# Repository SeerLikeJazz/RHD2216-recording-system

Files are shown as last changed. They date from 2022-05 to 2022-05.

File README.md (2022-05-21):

> 2022.05.21，上海，疫情在家，整理一下研究生期间的部分工作……

*Project was part of my work while at:*
* [EE-MEMS LAB](https://mems.sjtu.edu.cn/)
* Department of Micro/Nano Electronics
* Shanghai Jiao Tong University
* 2016.09-2019.03
### 探针型柔性MEMS脑机接口器件及采集电路研究
#### 系统介绍
* 研制了一种超薄的柔性探针型神经信号采集电极。
* 搭建了植入式神经信号采集电路的系统平台。
* 利用研制的柔性探针型神经信号采集电极和神经信号采集电路的系统平台做了体外测试验证实验。
#### 采集电路
电路主要包括Intan Technologies公司的16通道前端微弱生理信号采集芯片RHD2116，核心控制单元采用ST公司主频168M的STM32F407微控制器，数据传输采用内部集成全硬件TCP/IP协议栈+MAC+PHY以太网接口芯片W5500，通过UDP协议的方式实现硬件系统与上位机通信。

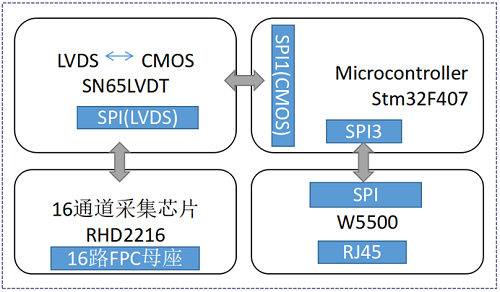
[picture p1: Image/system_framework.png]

> 系统框图

电路尺寸4.2cm x 4.2cm，重量22g（包含电池），可以非常轻便地用于脑机接口应用和生物学实验。实验表明，16通道的采集系统输入噪声低至7 μV，每通道采样频率高达20 kHz，采样分辨率16位，满足植入式神经信号采集的要求。

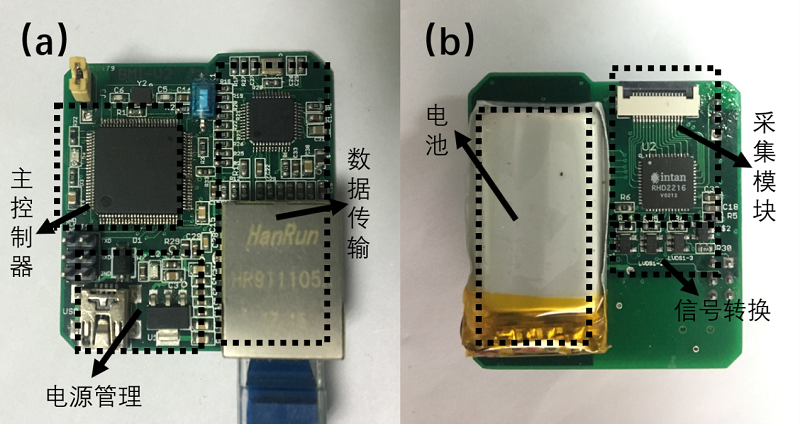
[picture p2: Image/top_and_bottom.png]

> 硬件顶、底视图

#### 柔性电极
器件整体全部采用生物相容性材料，Au（厚度300nm）作为引线、电极点和焊盘，Parylene（厚度4μm）作为基底和绝缘层，PEG作为粘结材料贴附电极于PI管上，PI管（外径330μm）用作辅助植入的支撑材料。

通过电化学沉积导电聚合物PEDOT:PSS来提高了电极的电化学性能，并通过500次的循环伏安测试和10分钟的超声处理，验证了修饰后的电极的电化学稳定和聚合物结合力稳定性，测试并分析了电极的伏安特性和电化学阻抗谱。

研究了通过生物相容性的材料和PI管的组合，改进了柔性电极的准确植入位置的方法。

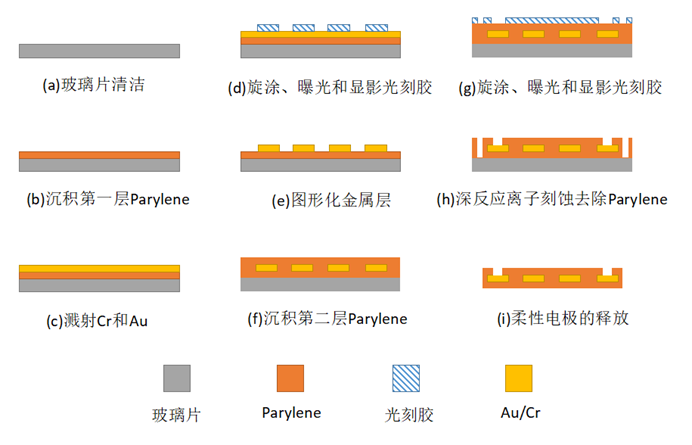
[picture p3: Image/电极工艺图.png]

> 电极工艺图

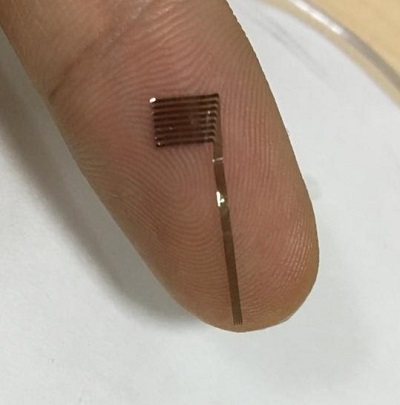
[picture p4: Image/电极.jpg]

> 电极实物图

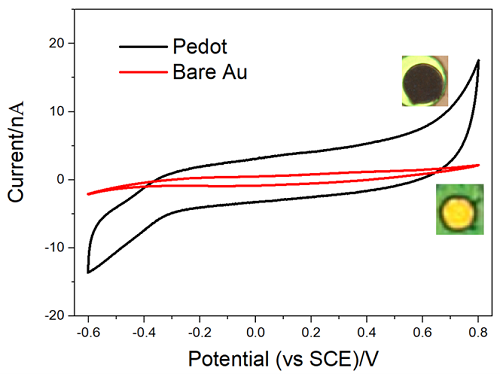
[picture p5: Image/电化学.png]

> 电化学测试

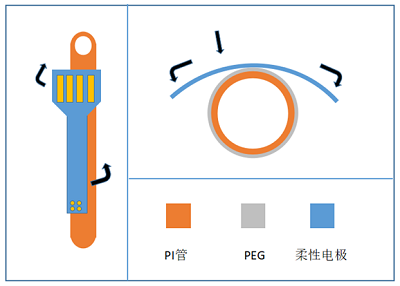
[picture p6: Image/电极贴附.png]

> 电极贴附示意图

#### 实验测试
为了验证从电极前端到采集电路后端整个系统的准确性和功能稳定性，使用琼脂和PBS溶液模拟脑组织的环境，验证柔性微电极的准确植入性，辅助使用PI管和柔性电极在环境中的分离状况；使用微小信号发生器模拟了神经信号的幅值和频率，在体外模拟的脑组织环境中测试了信号采集、数据预处理、数据传输到上位机和上位机实时波形显示的在线实验。

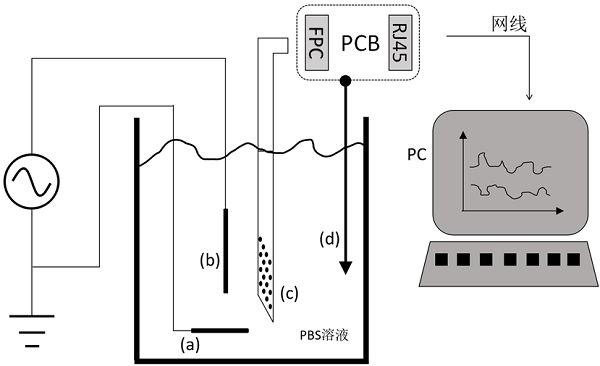
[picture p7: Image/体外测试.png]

> 测试实验示意图

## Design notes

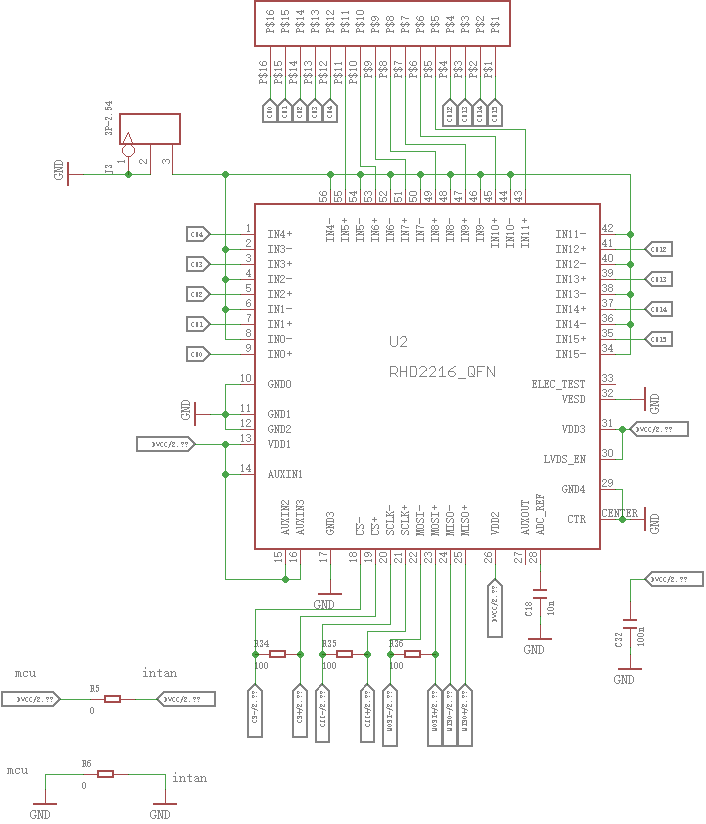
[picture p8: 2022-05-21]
Hardware/sheet 4-RHD2216.png

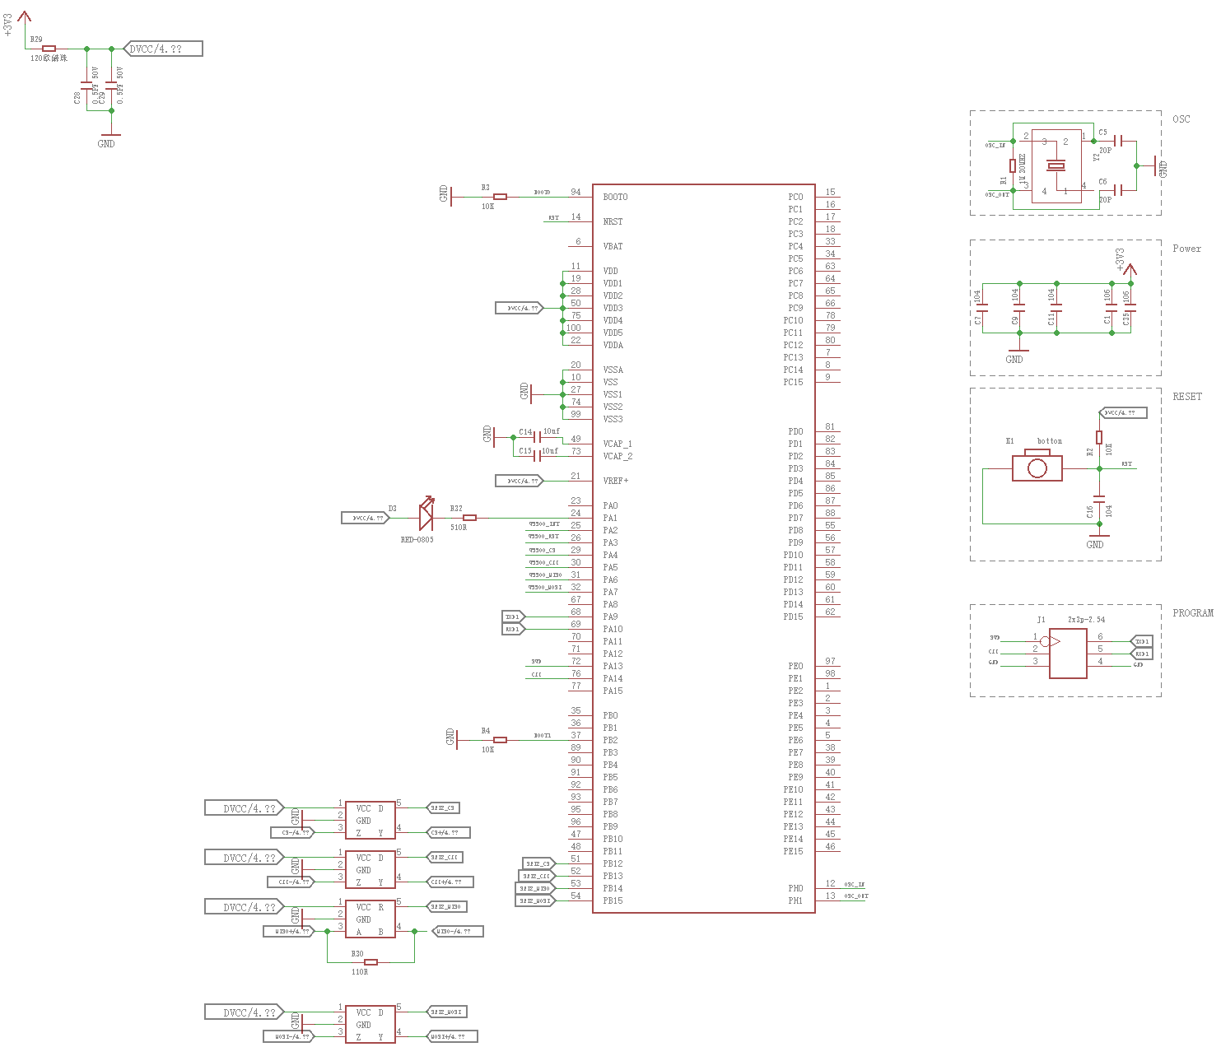
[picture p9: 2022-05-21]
Hardware/sheet 2-Mcu.png

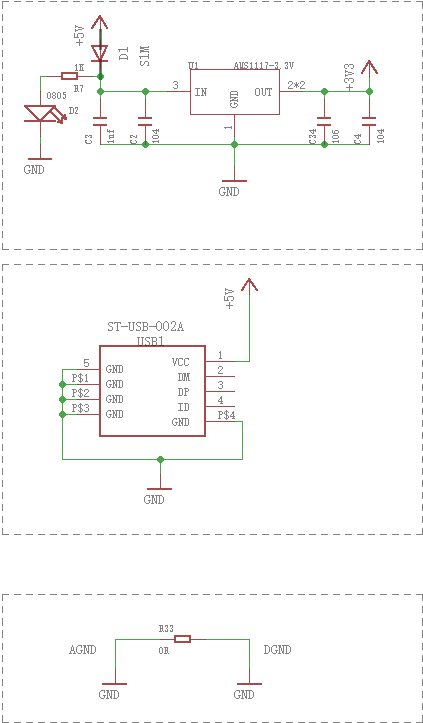
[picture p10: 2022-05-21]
Hardware/sheet 1-Power.png

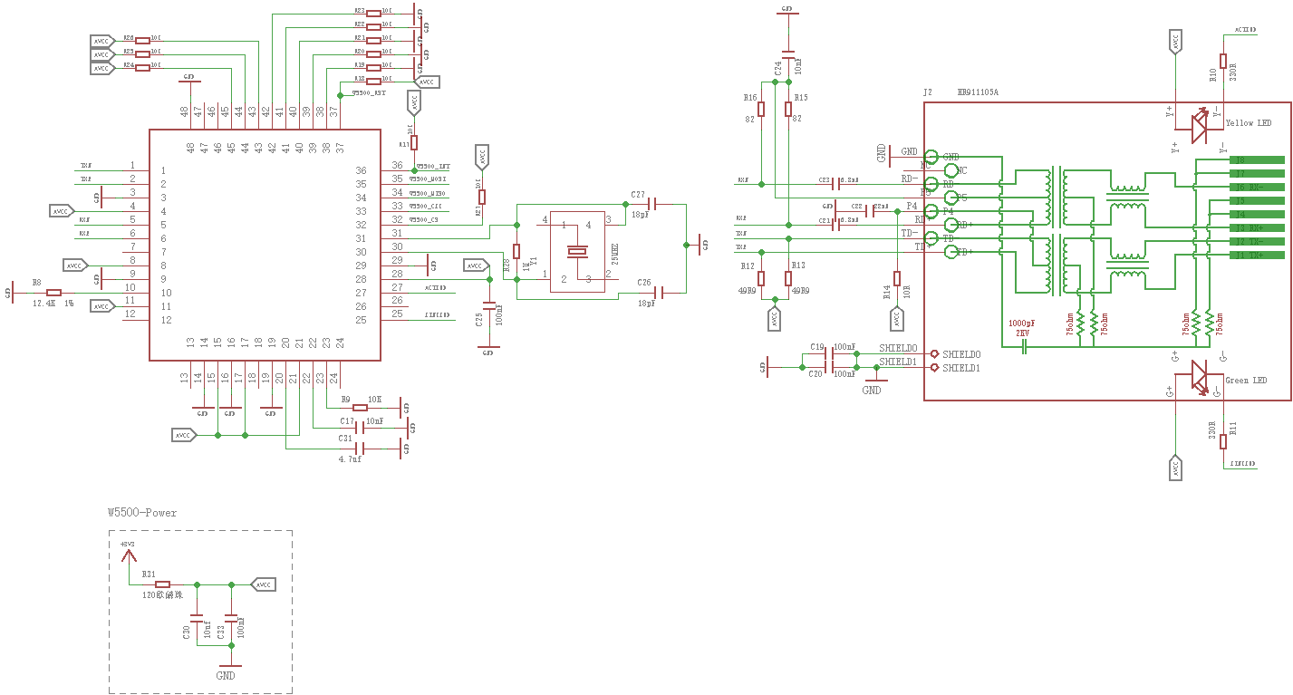
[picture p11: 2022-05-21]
Hardware/sheet 3-W5500.png

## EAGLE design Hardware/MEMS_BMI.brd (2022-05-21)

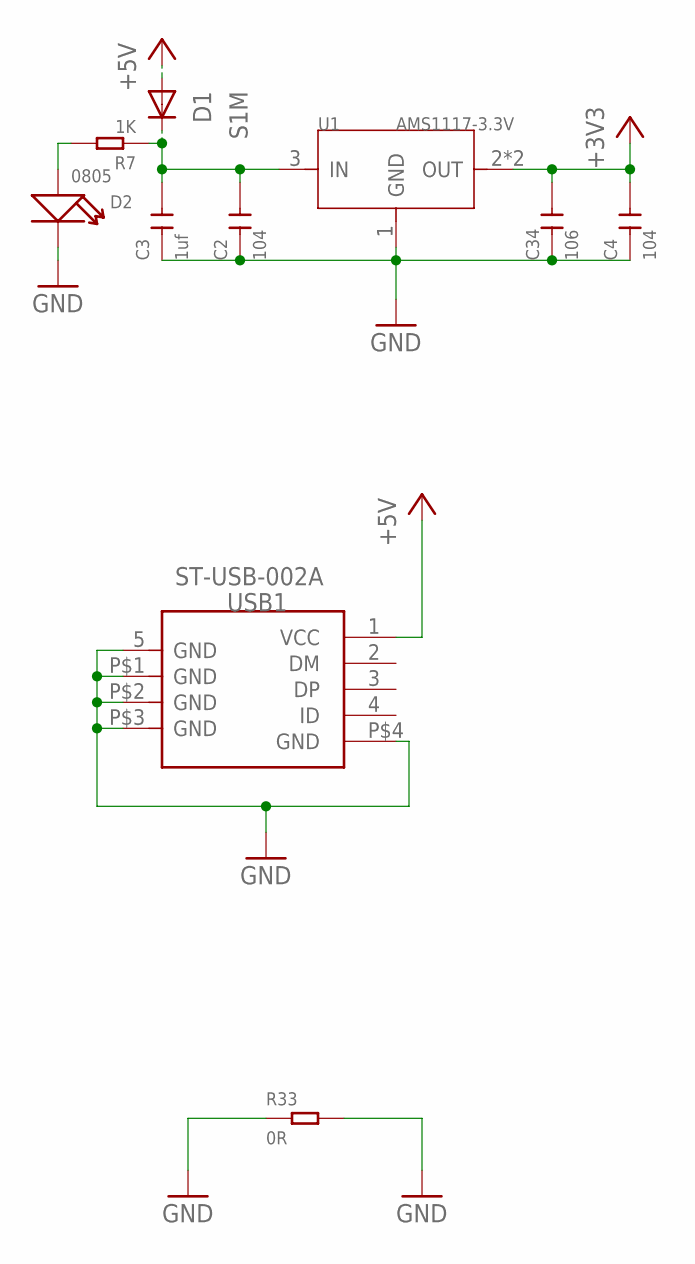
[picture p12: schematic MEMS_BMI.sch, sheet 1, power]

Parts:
C2, C4: 104; C0603
C3: 1uf; C0805
C34: 106; C0805
D1: S1M; SMA
D2: 0805; LED-0805
R7: 1K; R0603
R33: 0R; R0603
U1: AMS1117-3.3V; SOT-223
USB1: ST-USB-002A; MINIUSB5+4P-SMD-0.8-90D

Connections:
+3V3: C4.2, C34.2, U1.2 (OUT), U1.TER (OUT); also elsewhere on the board
+5V: D1.A, USB1.1 (VCC)
GND: C2.1, C3.1, C4.1, C34.1, D2.-, R33.1, R33.2, U1.1 (GND), USB1.5 (GND), USB1.P$1 (GND), USB1.P$2 (GND), USB1.P$3 (GND), USB1.P$4 (GND); also elsewhere on the board
unnamed: C2.2, C3.2, D1.C, R7.1, U1.3 (IN)
unnamed: D2.+, R7.2

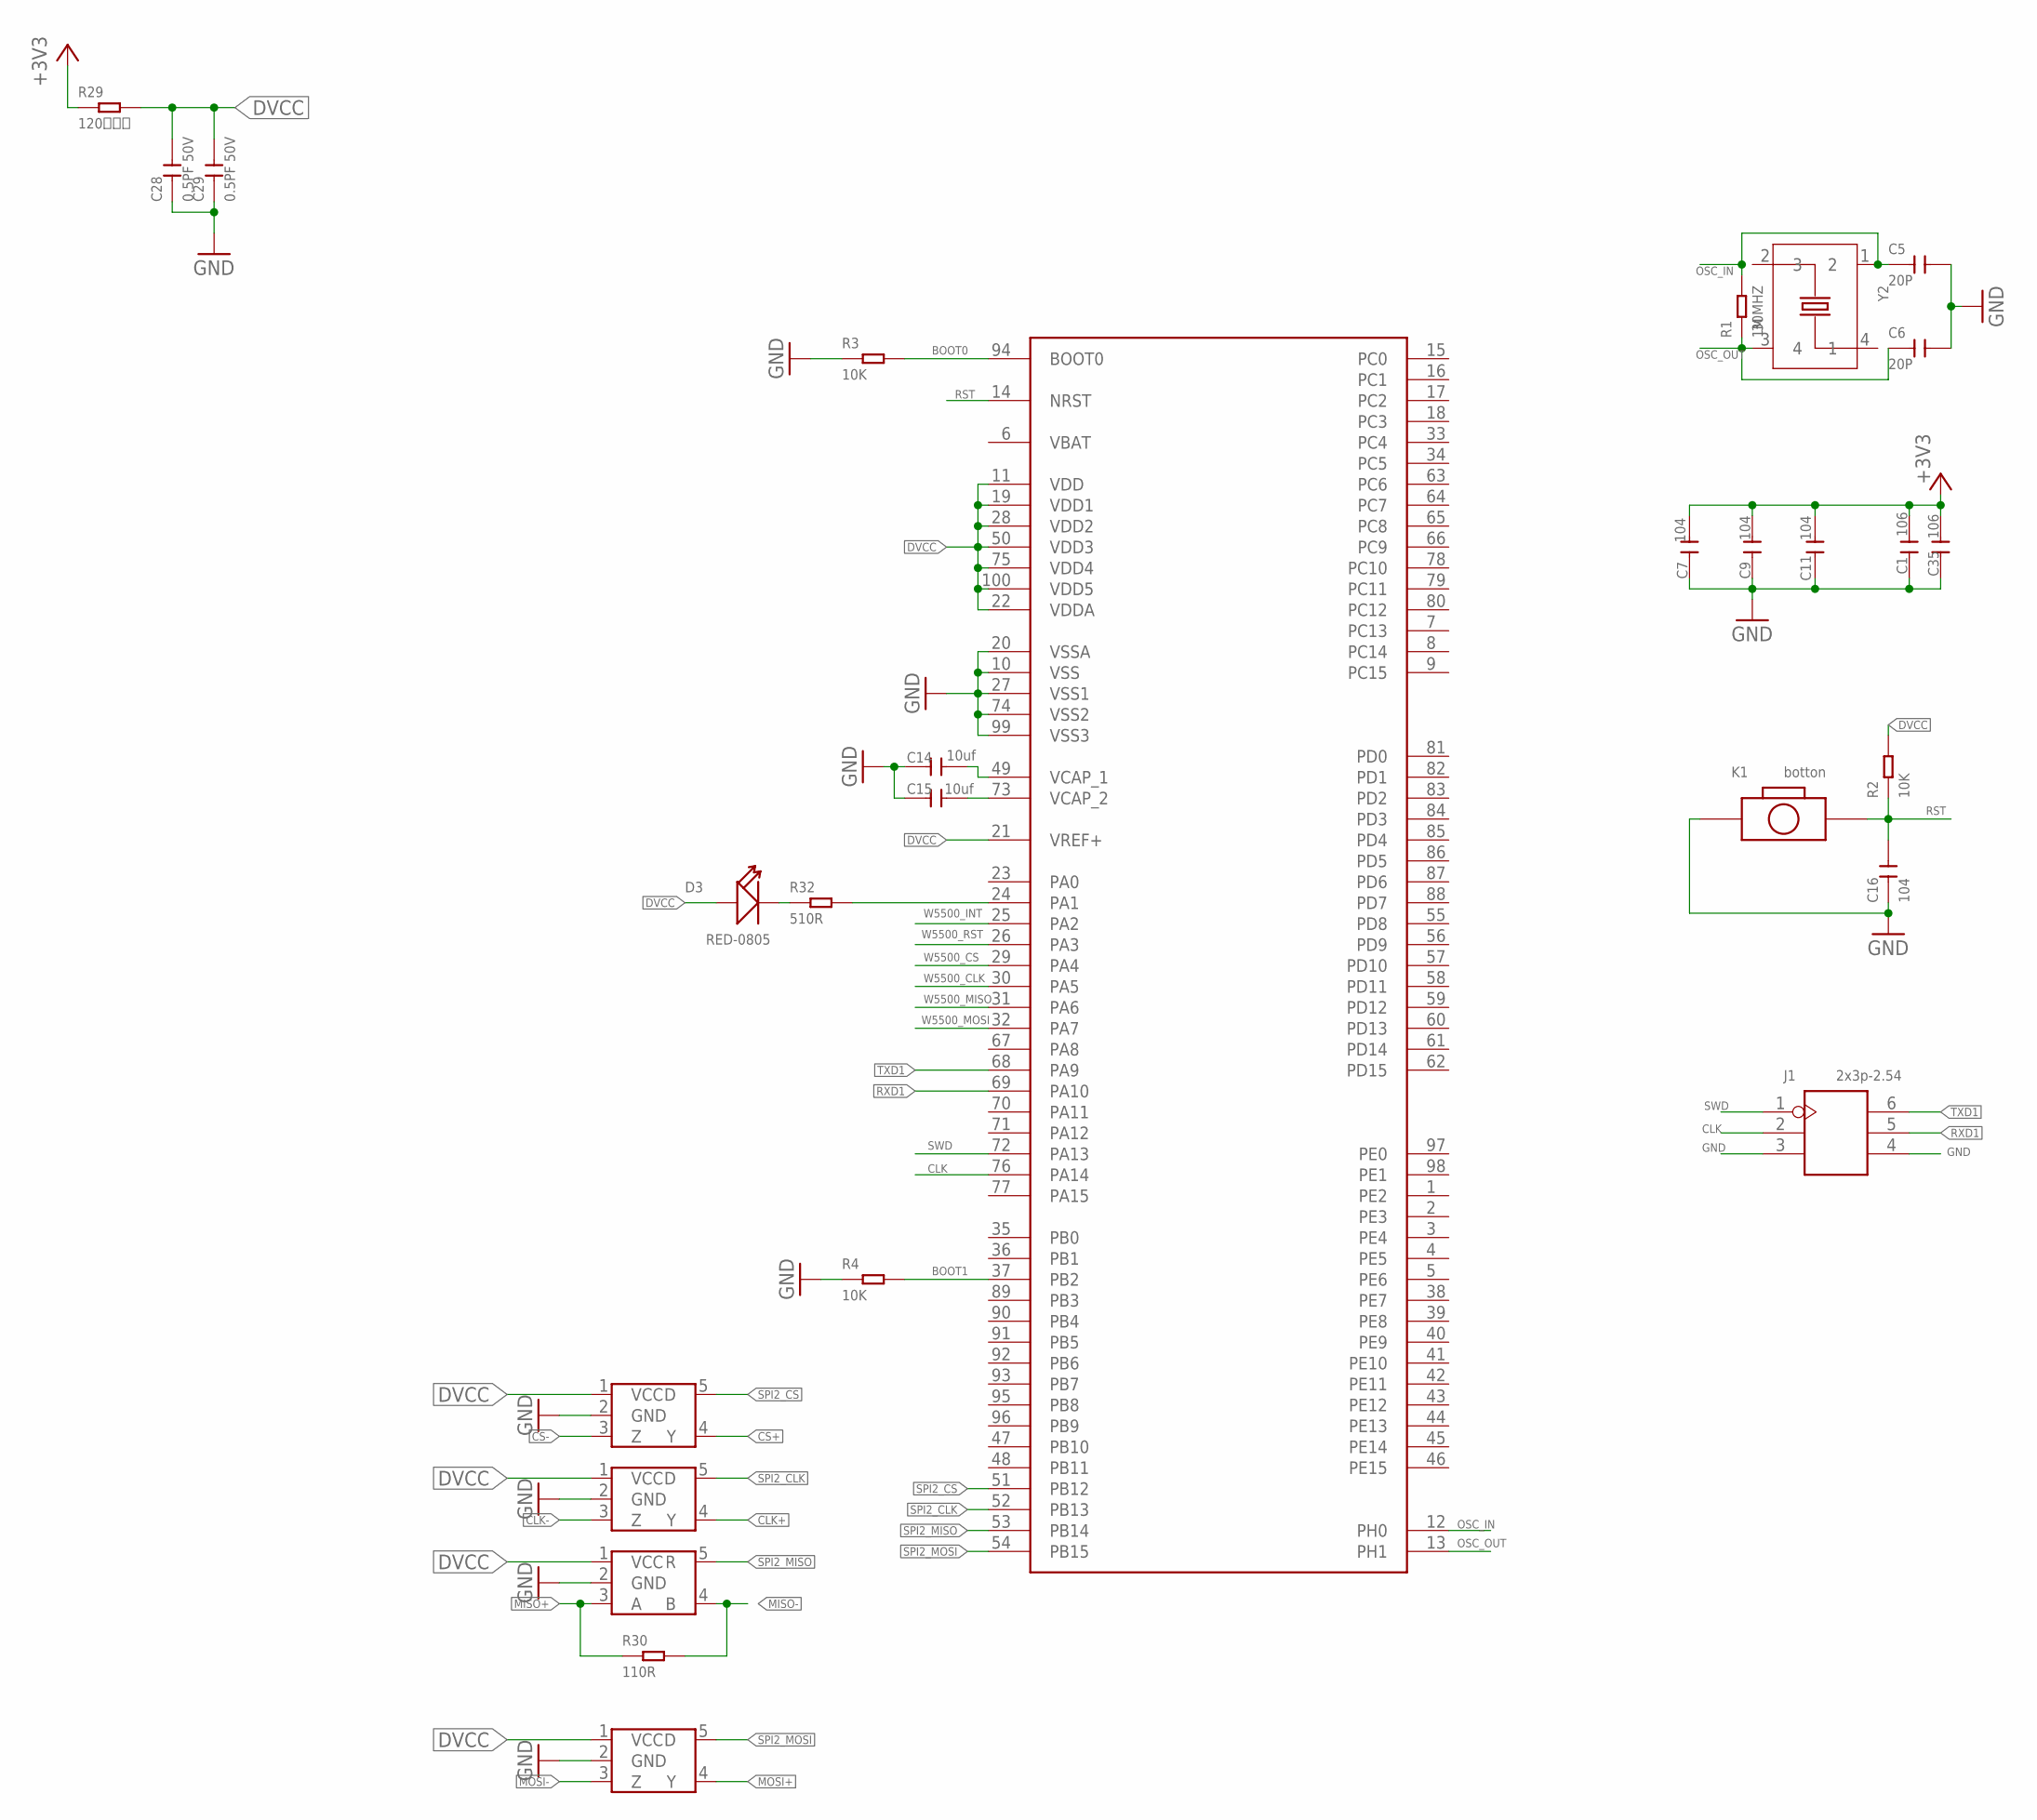
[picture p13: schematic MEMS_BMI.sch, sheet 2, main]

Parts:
C1, C35: 106; C0805
C5, C6: 20P; C0603
C7, C9, C11, C16: 104; C0603
C14, C15: 10uf; C0805
C28, C29: 0.5PF 50V; C0603
D3: RED-0805; LED-0805
J1: 2x3p-2.54; H2X3-2.54
K1: botton; SW2-SMD-3.0X6.0*2.5
LVDS1-1, LVDS1-2, LVDS1-3: SN65LVDS1; DBV_R-PDSO-G5
R1: 1M; R0603
R2, R3, R4: 10K; R0603
R29: 120欧磁珠; R0603
R30: 110R; R0603
R32: 510R; R0603
U$1: STM32F40XSTM32D40X; LQFP100
U$2: SN65LVDS2; DBV_R-PDSO-G5
Y2: 30MHZ; X4-SMD-3.2X2.5X0.7MM

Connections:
+3V3: C1.2, C7.1, C9.1, C11.1, C35.2, R29.1; also elsewhere on the board
BOOT0: R3.2, U$1.94 (BOOT0)
BOOT1: R4.2, U$1.37 (PB2)
CLK: J1.2, U$1.76 (PA14)
CLK+: LVDS1-2.4 (Y); also elsewhere on the board
CLK-: LVDS1-2.3 (Z); also elsewhere on the board
CS+: LVDS1-1.4 (Y); also elsewhere on the board
CS-: LVDS1-1.3 (Z); also elsewhere on the board
DVCC: C28.2, C29.2, D3.+, LVDS1-1.1 (VCC), LVDS1-2.1 (VCC), LVDS1-3.1 (VCC), R2.2, R29.2, U$1.11 (VDD), U$1.19 (VDD1), U$1.21 (VREF+), U$1.22 (VDDA), U$1.28 (VDD2), U$1.50 (VDD3), U$1.75 (VDD4), U$1.100 (VDD5), U$2.1 (VCC); also elsewhere on the board
GND: C1.1, C5.2, C6.2, C7.2, C9.2, C11.2, C14.1, C15.1, C16.1, C28.1, C29.1, C35.1, J1.3, J1.4, K1.1, LVDS1-1.2 (GND), LVDS1-2.2 (GND), LVDS1-3.2 (GND), R3.1, R4.1, U$1.10 (VSS), U$1.20 (VSSA), U$1.27 (VSS1), U$1.74 (VSS2), U$1.99 (VSS3), U$2.2 (GND); also elsewhere on the board
MISO+: R30.1, U$2.3 (A); also elsewhere on the board
MISO-: R30.2, U$2.4 (B); also elsewhere on the board
MOSI+: LVDS1-3.4 (Y); also elsewhere on the board
MOSI-: LVDS1-3.3 (Z); also elsewhere on the board
unnamed: C15.2, U$1.73 (VCAP_2)
unnamed: C14.2, U$1.49 (VCAP_1)
unnamed: D3.-, R32.1
unnamed: R32.2, U$1.24 (PA1)
OSC_IN: C5.1, R1.2, U$1.12 (PH0), Y2.1 (2)
OSC_OUT: C6.1, R1.1, U$1.13 (PH1), Y2.3 (4)
RST: C16.2, K1.2, R2.1, U$1.14 (NRST)
RXD1: J1.5, U$1.69 (PA10)
SPI2_CLK: LVDS1-2.5 (D), U$1.52 (PB13)
SPI2_CS: LVDS1-1.5 (D), U$1.51 (PB12)
SPI2_MISO: U$1.53 (PB14), U$2.5 (R)
SPI2_MOSI: LVDS1-3.5 (D), U$1.54 (PB15)
SWD: J1.1, U$1.72 (PA13)
TXD1: J1.6, U$1.68 (PA9)
W5500_CLK: U$1.30 (PA5); also elsewhere on the board
W5500_CS: U$1.29 (PA4); also elsewhere on the board
W5500_INT: U$1.25 (PA2); also elsewhere on the board
W5500_MISO: U$1.31 (PA6); also elsewhere on the board
W5500_MOSI: U$1.32 (PA7); also elsewhere on the board
W5500_RST: U$1.26 (PA3); also elsewhere on the board

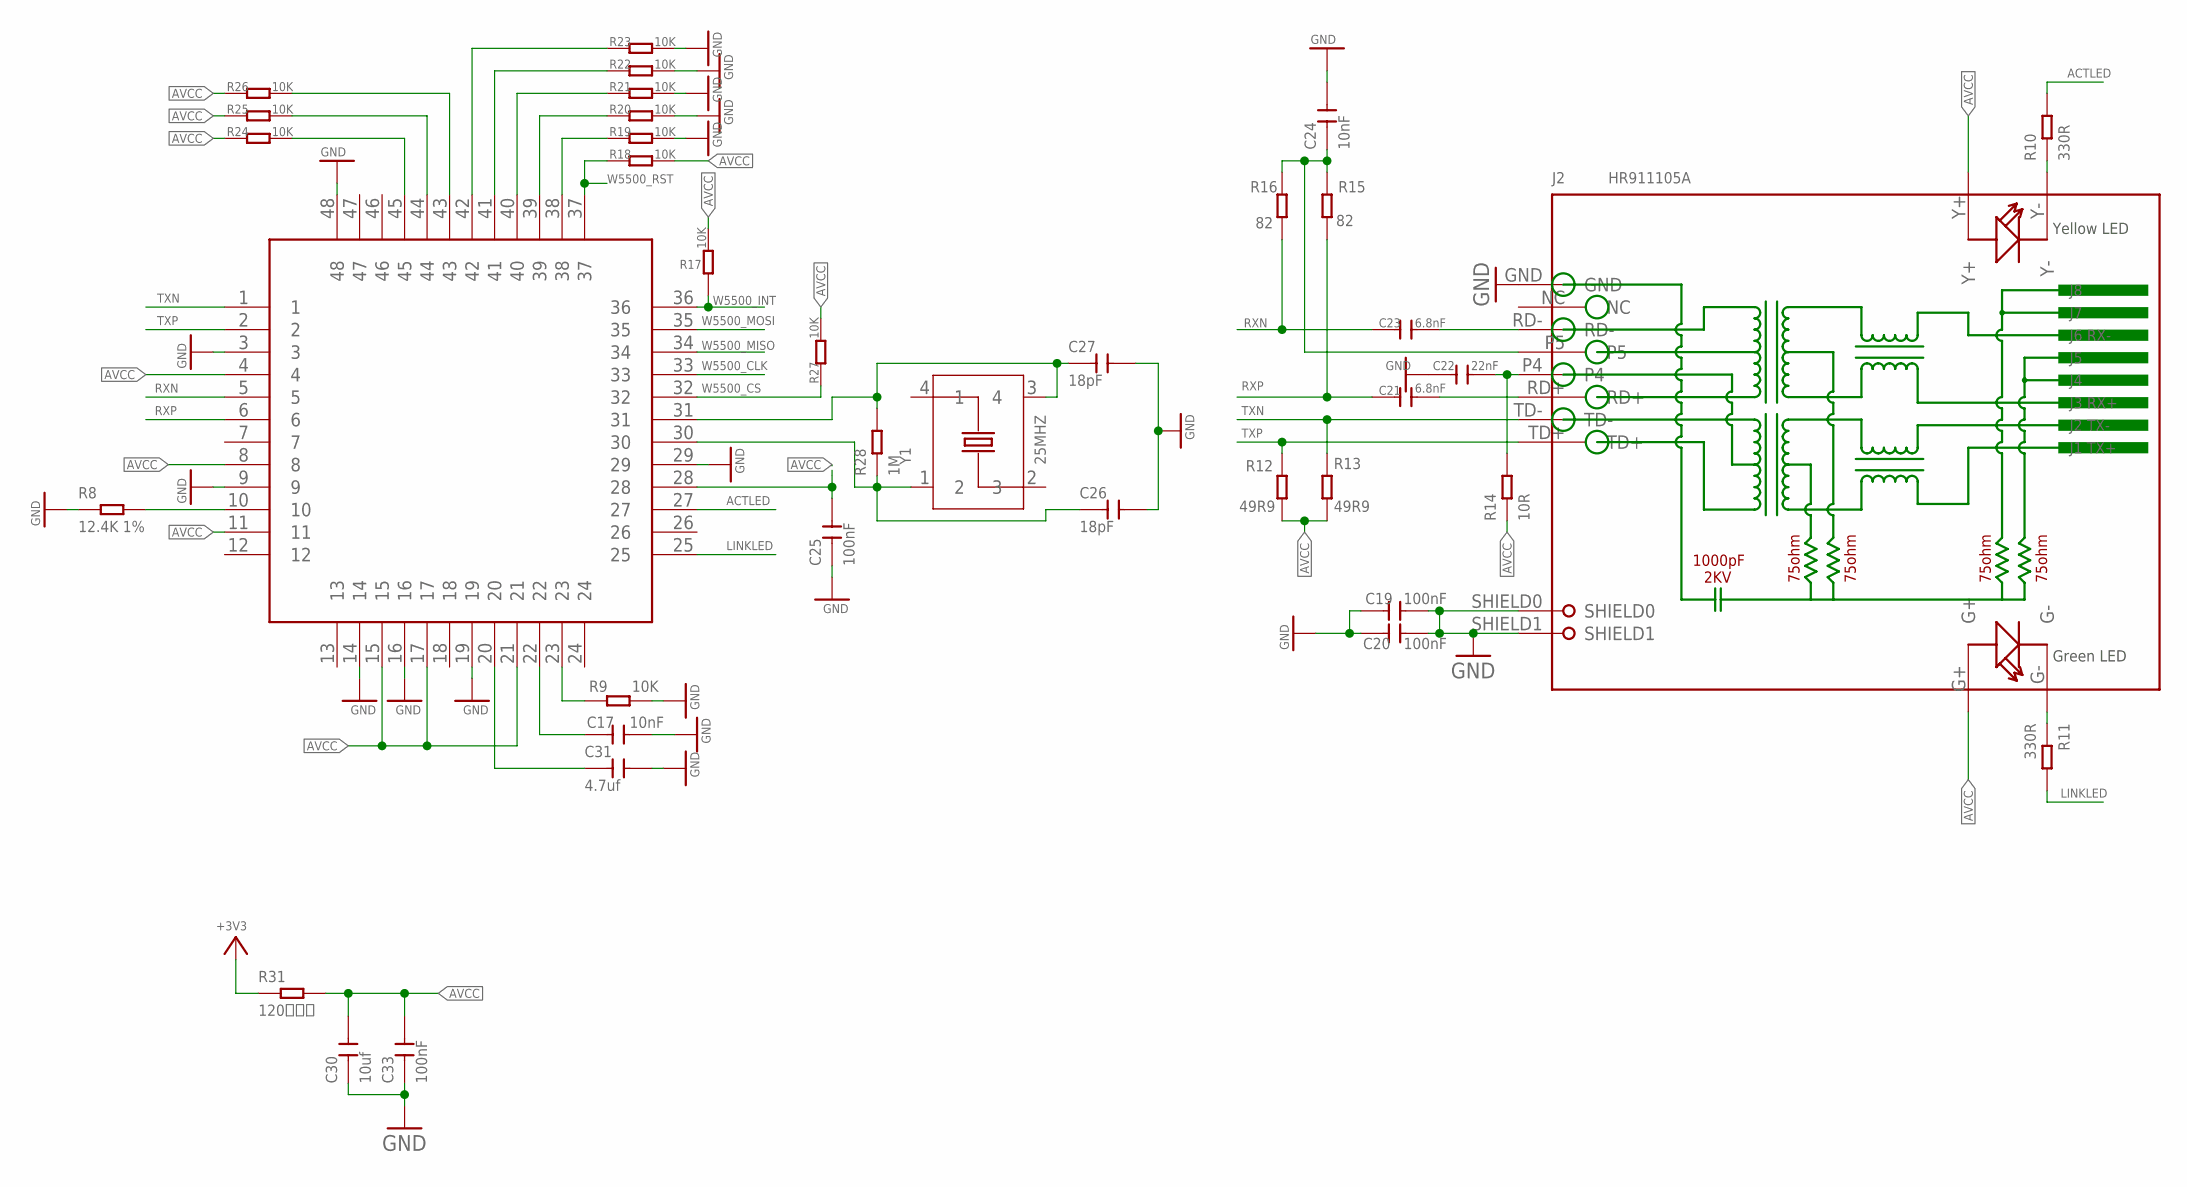
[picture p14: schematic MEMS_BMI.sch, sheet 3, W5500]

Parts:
C17, C24: 10nF; C0603
C19, C20, C25, C33: 100nF; C0603
C21, C23: 6.8nF; C0603
C22: 22nF; C0603
C26, C27: 18pF; C0603
C30: 10uf; C0805
C31: 4.7uf; C0805
J2: HR911105A; RJ45-12+2P-21.3X16.04X13.4MM
R8: 12.4K 1%; R0603
R9, R17, R18, R19, R20, R21, R22, R23, R24, R25, R26, R27: 10K; R0603
R10, R11: 330R; R0603
R12, R13: 49R9; R0603
R14: 10R; R0603
R15, R16: 82; R0603
R28: 1M; R0603
R31: 120欧磁珠; R0603
W5500-1: W5500; LQFP48
Y1: 25MHZ; X4-SMD-3.2X2.5X0.7MM

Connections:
+3V3: R31.1; also elsewhere on the board
ACTLED: R10.2, W5500-1.27
AVCC: C25.2, C30.2, C33.2, J2.G+, J2.Y+, R12.1, R13.1, R14.1, R17.2, R18.2, R24.1, R25.1, R26.1, R27.2, R31.2, W5500-1.4, W5500-1.8, W5500-1.11, W5500-1.15, W5500-1.17, W5500-1.21, W5500-1.28
GND: C17.2, C19.1, C19.2, C20.1, C20.2, C22.1, C24.2, C25.1, C26.2, C27.2, C30.1, C31.2, C33.1, J2.GND, J2.SHIELD0, J2.SHIELD1, R8.1, R9.2, R19.2, R20.2, R21.2, R22.2, R23.2, W5500-1.3, W5500-1.9, W5500-1.14, W5500-1.16, W5500-1.19, W5500-1.29, W5500-1.48; also elsewhere on the board
LINKLED: R11.2, W5500-1.25
unnamed: R9.1, W5500-1.23
unnamed: C17.1, W5500-1.22
unnamed: C31.1, W5500-1.20
unnamed: J2.G-, R11.1
unnamed: J2.Y-, R10.1
unnamed: R24.2, W5500-1.45
unnamed: R8.2, W5500-1.10
unnamed: R25.2, W5500-1.44
unnamed: C21.2, J2.RD+
unnamed: C22.2, J2.P4, R14.2
unnamed: R26.2, W5500-1.43
unnamed: C23.2, J2.RD-
unnamed: C27.1, R28.2, W5500-1.31, Y1.3 (4)
unnamed: R19.1, W5500-1.38
unnamed: C24.1, J2.P5, R15.2, R16.2
unnamed: R20.1, W5500-1.39
unnamed: R21.1, W5500-1.40
unnamed: R22.1, W5500-1.41
unnamed: R23.1, W5500-1.42
unnamed: C26.1, R28.1, W5500-1.30, Y1.1 (2)
RXN: C23.1, R16.1, W5500-1.5
RXP: C21.1, R15.1, W5500-1.6
TXN: J2.TD-, R13.2, W5500-1.1
TXP: J2.TD+, R12.2, W5500-1.2
W5500_CLK: W5500-1.33; also elsewhere on the board
W5500_CS: R27.1, W5500-1.32; also elsewhere on the board
W5500_INT: R17.1, W5500-1.36; also elsewhere on the board
W5500_MISO: W5500-1.34; also elsewhere on the board
W5500_MOSI: W5500-1.35; also elsewhere on the board
W5500_RST: R18.1, W5500-1.37; also elsewhere on the board

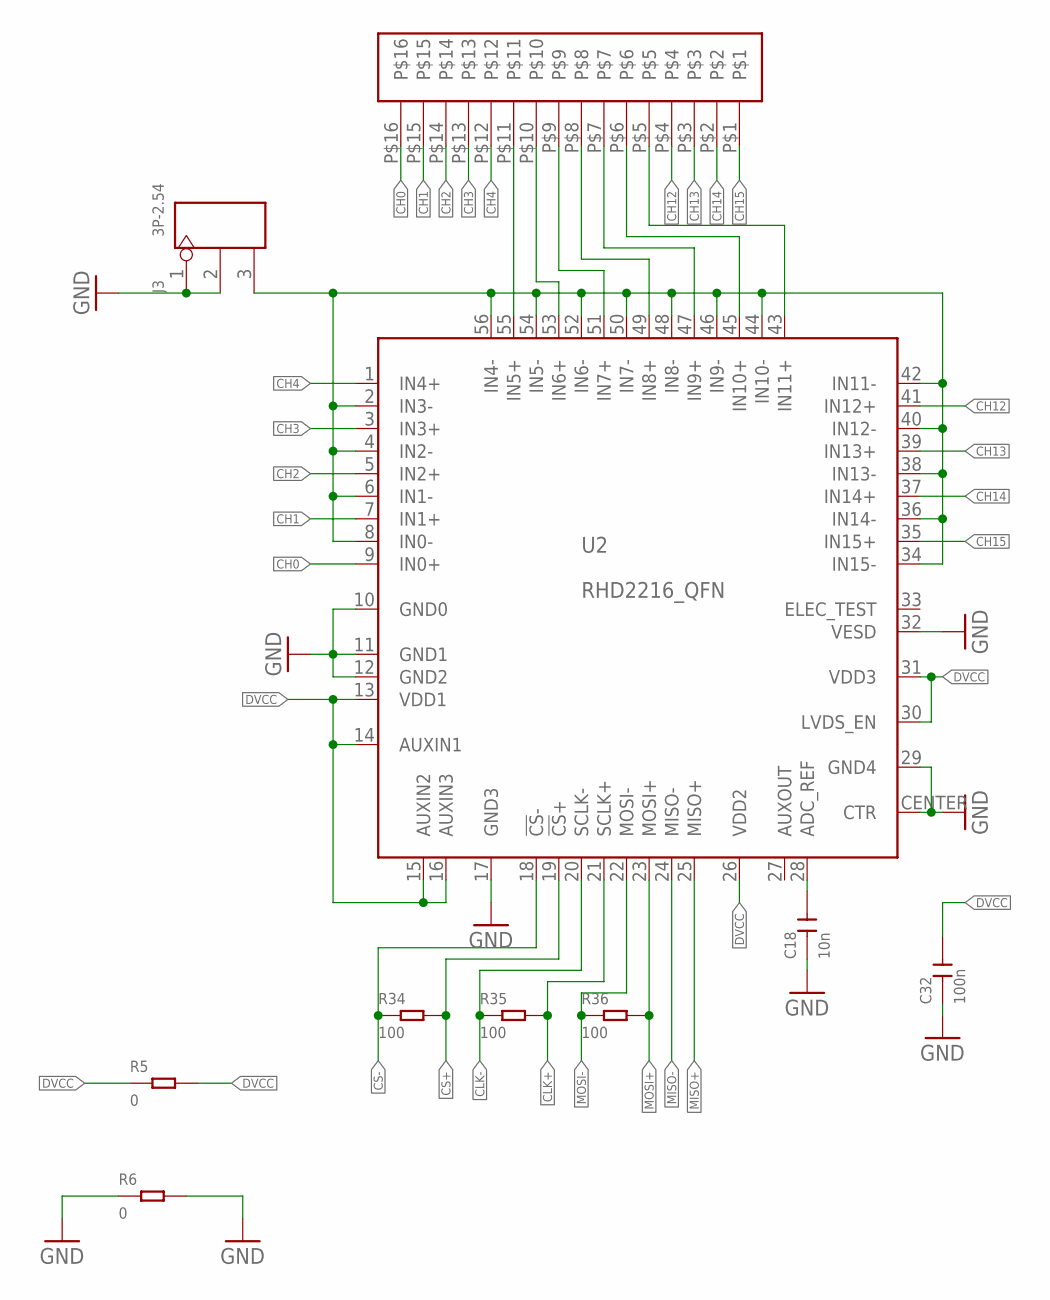
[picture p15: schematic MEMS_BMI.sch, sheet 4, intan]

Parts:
C18: 10n; C0603
C32: 100n; C0603
J3: 3P-2.54; H3-2.54
R5, R6: 0; R0603
R34, R35, R36: 100; R0603
U2: RHD2216_QFN; QFN56_8_X_8_LARGE
U$3: PROBE; PROBE-16-PIN

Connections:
CH0: U2.9 (IN0+), U$3.P$16
CH1: U2.7 (IN1+), U$3.P$15
CH2: U2.5 (IN2+), U$3.P$14
CH3: U2.3 (IN3+), U$3.P$13
CH4: U2.1 (IN4+), U$3.P$12
CH12: U2.41 (IN12+), U$3.P$4
CH13: U2.39 (IN13+), U$3.P$3
CH14: U2.37 (IN14+), U$3.P$2
CH15: U2.35 (IN15+), U$3.P$1
CLK+: R35.2, U2.21 (SCLK+); also elsewhere on the board
CLK-: R35.1, U2.20 (SCLK-); also elsewhere on the board
CS+: R34.2, U2.19 (!CS!+); also elsewhere on the board
CS-: R34.1, U2.18 (!CS!-); also elsewhere on the board
DVCC: C32.2, R5.1, R5.2, U2.13 (VDD1), U2.14 (AUXIN1), U2.15 (AUXIN2), U2.16 (AUXIN3), U2.26 (VDD2), U2.30 (LVDS_EN), U2.31 (VDD3); also elsewhere on the board
GND: C18.1, C32.1, J3.1, J3.2, R6.1, R6.2, U2.10 (GND0), U2.11 (GND1), U2.12 (GND2), U2.17 (GND3), U2.29 (GND4), U2.32 (VESD), U2.CENTER (CTR); also elsewhere on the board
MISO+: U2.25 (MISO+); also elsewhere on the board
MISO-: U2.24 (MISO-); also elsewhere on the board
MOSI+: R36.2, U2.23 (MOSI+); also elsewhere on the board
MOSI-: R36.1, U2.22 (MOSI-); also elsewhere on the board
unnamed: C18.2, U2.28 (ADC_REF)
unnamed: J3.3, U2.2 (IN3-), U2.4 (IN2-), U2.6 (IN1-), U2.8 (IN0-), U2.34 (IN15-), U2.36 (IN14-), U2.38 (IN13-), U2.40 (IN12-), U2.42 (IN11-), U2.44 (IN10-), U2.46 (IN9-), U2.48 (IN8-), U2.50 (IN7-), U2.52 (IN6-), U2.54 (IN5-), U2.56 (IN4-)
unnamed: U2.55 (IN5+), U$3.P$11
unnamed: U2.53 (IN6+), U$3.P$10
unnamed: U2.51 (IN7+), U$3.P$9
unnamed: U2.49 (IN8+), U$3.P$8
unnamed: U2.47 (IN9+), U$3.P$7
unnamed: U2.45 (IN10+), U$3.P$6
unnamed: U2.43 (IN11+), U$3.P$5

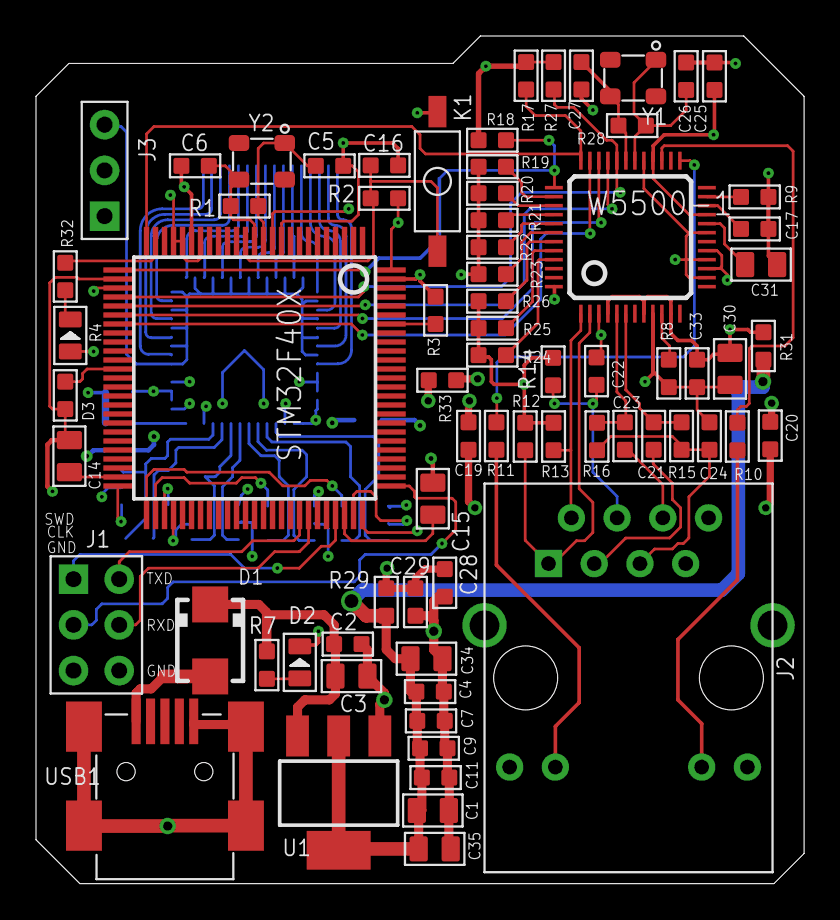
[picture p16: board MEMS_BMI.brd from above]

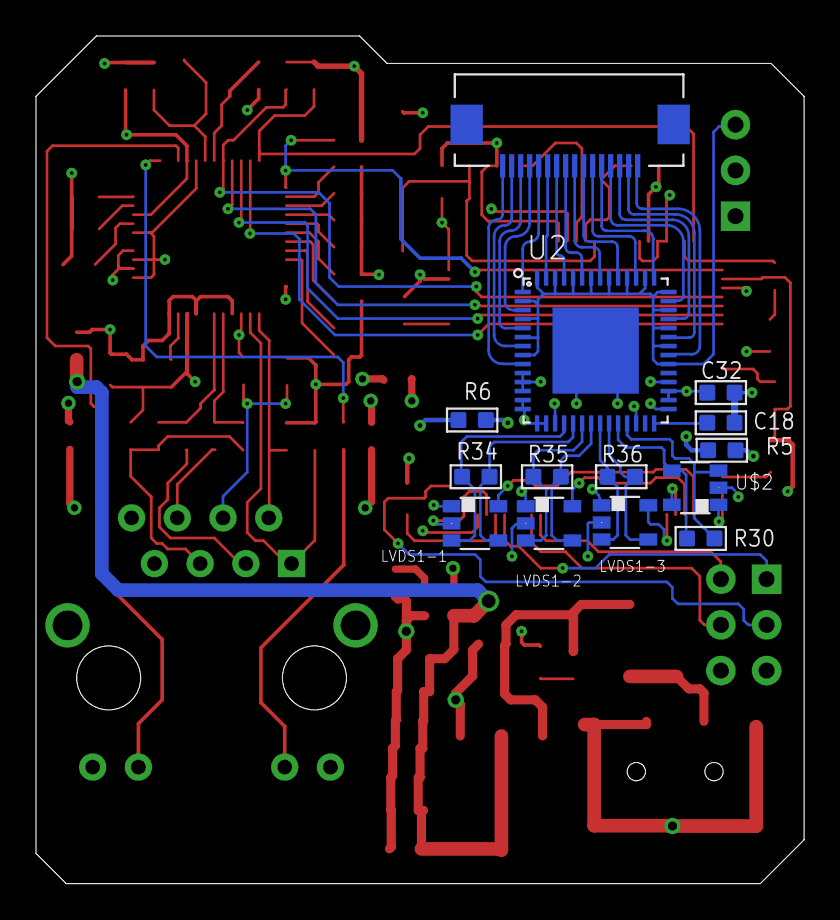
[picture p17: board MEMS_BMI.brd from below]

Board: 4 copper layers, 42.7 x 47.1 mm, 86 parts (14 on the bottom side), 82 nets.

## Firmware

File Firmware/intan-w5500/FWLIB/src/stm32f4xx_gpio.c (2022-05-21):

/**
  ******************************************************************************
  * @file    stm32f4xx_gpio.c
  * @author  MCD Application Team
  * @version V1.4.0
  * @date    04-August-2014
  * @brief   This file provides firmware functions to manage the following 
  *          functionalities of the GPIO peripheral:           
  *           + Initialization and Configuration
  *           + GPIO Read and Write
  *           + GPIO Alternate functions configuration
  * 
@verbatim  
 ===============================================================================
                      ##### How to use this driver #####
 ===============================================================================       
 [..]             
   (#) Enable the GPIO AHB clock using the following function
       RCC_AHB1PeriphClockCmd(RCC_AHB1Periph_GPIOx, ENABLE);
               
   (#) Configure the GPIO pin(s) using GPIO_Init()
       Four possible configuration are available for each pin:
       (++) Input: Floating, Pull-up, Pull-down.
       (++) Output: Push-Pull (Pull-up, Pull-down or no Pull)
            Open Drain (Pull-up, Pull-down or no Pull). In output mode, the speed 
            is configurable: 2 MHz, 25 MHz, 50 MHz or 100 MHz.
       (++) Alternate Function: Push-Pull (Pull-up, Pull-down or no Pull) Open 
            Drain (Pull-up, Pull-down or no Pull).
       (++) Analog: required mode when a pin is to be used as ADC channel or DAC 
            output.
   
   (#) Peripherals alternate function:
       (++) For ADC and DAC, configure the desired pin in analog mode using 
            GPIO_InitStruct->GPIO_Mode = GPIO_Mode_AN;
            (+++) For other peripherals (TIM, USART...):
            (+++) Connect the pin to the desired peripherals' Alternate 
                     Function (AF) using GPIO_PinAFConfig() function
            (+++) Configure the desired pin in alternate function mode using
                     GPIO_InitStruct->GPIO_Mode = GPIO_Mode_AF
            (+++) Select the type, pull-up/pull-down and output speed via 
                     GPIO_PuPd, GPIO_OType and GPIO_Speed members
            (+++) Call GPIO_Init() function
          
   (#) To get the level of a pin configured in input mode use GPIO_ReadInputDataBit()
            
   (#) To set/reset the level of a pin configured in output mode use 
       GPIO_SetBits()/GPIO_ResetBits()
                 
   (#) During and just after reset, the alternate functions are not 
       active and the GPIO pins are configured in input floating mode (except JTAG
       pins).
  
   (#) The LSE oscillator pins OSC32_IN and OSC32_OUT can be used as general purpose 
       (PC14 and PC15, respectively) when the LSE oscillator is off. The LSE has 
       priority over the GPIO function.
  
   (#) The HSE oscillator pins OSC_IN/OSC_OUT can be used as 
       general purpose PH0 and PH1, respectively, when the HSE oscillator is off. 
       The HSE has priority over the GPIO function.
               
@endverbatim        
  *
  ******************************************************************************
  * @attention
  *
  * <h2><center>&copy; COPYRIGHT 2014 STMicroelectronics</center></h2>
  *
  * Licensed under MCD-ST Liberty SW License Agreement V2, (the "License");
  * You may not use this file except in compliance with the License.
  * You may obtain a copy of the License at:
  *
  *        http://www.st.com/software_license_agreement_liberty_v2
  *
  * Unless required by applicable law or agreed to in writing, software 
  * distributed under the License is distributed on an "AS IS" BASIS, 
  * WITHOUT WARRANTIES OR CONDITIONS OF ANY KIND, either express or implied.
  * See the License for the specific language governing permissions and
  * limitations under the License.
  *
  ******************************************************************************
  */

/* Includes ------------------------------------------------------------------*/
#include "stm32f4xx_gpio.h"
#include "stm32f4xx_rcc.h"

/** @addtogroup STM32F4xx_StdPeriph_Driver
  * @{
  */

/** @defgroup GPIO 
  * @brief GPIO driver modules
  * @{
  */ 

/* Private typedef -----------------------------------------------------------*/
/* Private define ------------------------------------------------------------*/
/* Private macro -------------------------------------------------------------*/
/* Private variables ---------------------------------------------------------*/
/* Private function prototypes -----------------------------------------------*/
/* Private functions ---------------------------------------------------------*/

/** @defgroup GPIO_Private_Functions
  * @{
  */ 

/** @defgroup GPIO_Group1 Initialization and Configuration
 *  @brief   Initialization and Configuration
 *
@verbatim   
 ===============================================================================
                 ##### Initialization and Configuration #####
 ===============================================================================  

@endverbatim
  * @{
  */

/**
  * @brief  De-initializes the GPIOx peripheral registers to their default reset values.
  * @note   By default, The GPIO pins are configured in input floating mode (except JTAG pins).
  * @param  GPIOx: where x can be (A..K) to select the GPIO peripheral for STM32F405xx/407xx and STM32F415xx/417xx devices
  *                      x can be (A..I) to select the GPIO peripheral for STM32F42xxx/43xxx devices.
  *                      x can be (A, B, C, D and H) to select the GPIO peripheral for STM32F401xx devices.  
  * @retval None
  */
void GPIO_DeInit(GPIO_TypeDef* GPIOx)
{
  /* Check the parameters */
  assert_param(IS_GPIO_ALL_PERIPH(GPIOx));

  if (GPIOx == GPIOA)
  {
    RCC_AHB1PeriphResetCmd(RCC_AHB1Periph_GPIOA, ENABLE);
    RCC_AHB1PeriphResetCmd(RCC_AHB1Periph_GPIOA, DISABLE);
  }
  else if (GPIOx == GPIOB)
  {
    RCC_AHB1PeriphResetCmd(RCC_AHB1Periph_GPIOB, ENABLE);
    RCC_AHB1PeriphResetCmd(RCC_AHB1Periph_GPIOB, DISABLE);
  }
  else if (GPIOx == GPIOC)
  {
    RCC_AHB1PeriphResetCmd(RCC_AHB1Periph_GPIOC, ENABLE);
    RCC_AHB1PeriphResetCmd(RCC_AHB1Periph_GPIOC, DISABLE);
  }
  else if (GPIOx == GPIOD)
  {
    RCC_AHB1PeriphResetCmd(RCC_AHB1Periph_GPIOD, ENABLE);
    RCC_AHB1PeriphResetCmd(RCC_AHB1Periph_GPIOD, DISABLE);
  }
  else if (GPIOx == GPIOE)
  {
    RCC_AHB1PeriphResetCmd(RCC_AHB1Periph_GPIOE, ENABLE);
    RCC_AHB1PeriphResetCmd(RCC_AHB1Periph_GPIOE, DISABLE);
  }
  else if (GPIOx == GPIOF)
  {
    RCC_AHB1PeriphResetCmd(RCC_AHB1Periph_GPIOF, ENABLE);
    RCC_AHB1PeriphResetCmd(RCC_AHB1Periph_GPIOF, DISABLE);
  }
  else if (GPIOx == GPIOG)
  {
    RCC_AHB1PeriphResetCmd(RCC_AHB1Periph_GPIOG, ENABLE);
    RCC_AHB1PeriphResetCmd(RCC_AHB1Periph_GPIOG, DISABLE);
  }
  else if (GPIOx == GPIOH)
  {
    RCC_AHB1PeriphResetCmd(RCC_AHB1Periph_GPIOH, ENABLE);
    RCC_AHB1PeriphResetCmd(RCC_AHB1Periph_GPIOH, DISABLE);
  }

  else if (GPIOx == GPIOI)
  {
    RCC_AHB1PeriphResetCmd(RCC_AHB1Periph_GPIOI, ENABLE);
    RCC_AHB1PeriphResetCmd(RCC_AHB1Periph_GPIOI, DISABLE);
  }
  else if (GPIOx == GPIOJ)
  {
    RCC_AHB1PeriphResetCmd(RCC_AHB1Periph_GPIOJ, ENABLE);
    RCC_AHB1PeriphResetCmd(RCC_AHB1Periph_GPIOJ, DISABLE);
  }
  else
  {
    if (GPIOx == GPIOK)
    {
      RCC_AHB1PeriphResetCmd(RCC_AHB1Periph_GPIOK, ENABLE);
      RCC_AHB1PeriphResetCmd(RCC_AHB1Periph_GPIOK, DISABLE);
    }
  }
}

/**
  * @brief  Initializes the GPIOx peripheral according to the specified parameters in the GPIO_InitStruct.
  * @param  GPIOx: where x can be (A..K) to select the GPIO peripheral for STM32F405xx/407xx and STM32F415xx/417xx devices
  *                      x can be (A..I) to select the GPIO peripheral for STM32F42xxx/43xxx devices.
  *                      x can be (A, B, C, D and H) to select the GPIO peripheral for STM32F401xx devices.   
  * @param  GPIO_InitStruct: pointer to a GPIO_InitTypeDef structure that contains
  *         the configuration information for the specified GPIO peripheral.
  * @retval None
  */
void GPIO_Init(GPIO_TypeDef* GPIOx, GPIO_InitTypeDef* GPIO_InitStruct)
{
  uint32_t pinpos = 0x00, pos = 0x00 , currentpin = 0x00;

  /* Check the parameters */
  assert_param(IS_GPIO_ALL_PERIPH(GPIOx));
  assert_param(IS_GPIO_PIN(GPIO_InitStruct->GPIO_Pin));
  assert_param(IS_GPIO_MODE(GPIO_InitStruct->GPIO_Mode));
  assert_param(IS_GPIO_PUPD(GPIO_InitStruct->GPIO_PuPd));

  /* ------------------------- Configure the port pins ---------------- */
  /*-- GPIO Mode Configuration --*/
  for (pinpos = 0x00; pinpos < 0x10; pinpos++)
  {
    pos = ((uint32_t)0x01) << pinpos;
    /* Get the port pins position */
    currentpin = (GPIO_InitStruct->GPIO_Pin) & pos;

    if (currentpin == pos)
    {
      GPIOx->MODER  &= ~(GPIO_MODER_MODER0 << (pinpos * 2));
      GPIOx->MODER |= (((uint32_t)GPIO_InitStruct->GPIO_Mode) << (pinpos * 2));

      if ((GPIO_InitStruct->GPIO_Mode == GPIO_Mode_OUT) || (GPIO_InitStruct->GPIO_Mode == GPIO_Mode_AF))
      {
        /* Check Speed mode parameters */
        assert_param(IS_GPIO_SPEED(GPIO_InitStruct->GPIO_Speed));

        /* Speed mode configuration */
        GPIOx->OSPEEDR &= ~(GPIO_OSPEEDER_OSPEEDR0 << (pinpos * 2));
        GPIOx->OSPEEDR |= ((uint32_t)(GPIO_InitStruct->GPIO_Speed) << (pinpos * 2));

        /* Check Output mode parameters */
        assert_param(IS_GPIO_OTYPE(GPIO_InitStruct->GPIO_OType));

        /* Output mode configuration*/
        GPIOx->OTYPER  &= ~((GPIO_OTYPER_OT_0) << ((uint16_t)pinpos)) ;
        GPIOx->OTYPER |= (uint16_t)(((uint16_t)GPIO_InitStruct->GPIO_OType) << ((uint16_t)pinpos));
      }

      /* Pull-up Pull down resistor configuration*/
      GPIOx->PUPDR &= ~(GPIO_PUPDR_PUPDR0 << ((uint16_t)pinpos * 2));
      GPIOx->PUPDR |= (((uint32_t)GPIO_InitStruct->GPIO_PuPd) << (pinpos * 2));
    }
  }
}

/**
  * @brief  Fills each GPIO_InitStruct member with its default value.
  * @param  GPIO_InitStruct : pointer to a GPIO_InitTypeDef structure which will be initialized.
  * @retval None
  */
void GPIO_StructInit(GPIO_InitTypeDef* GPIO_InitStruct)
{
  /* Reset GPIO init structure parameters values */
  GPIO_InitStruct->GPIO_Pin  = GPIO_Pin_All;
  GPIO_InitStruct->GPIO_Mode = GPIO_Mode_IN;
  GPIO_InitStruct->GPIO_Speed = GPIO_Speed_2MHz;
  GPIO_InitStruct->GPIO_OType = GPIO_OType_PP;
  GPIO_InitStruct->GPIO_PuPd = GPIO_PuPd_NOPULL;
}

/**
  * @brief  Locks GPIO Pins configuration registers.
  * @note   The locked registers are GPIOx_MODER, GPIOx_OTYPER, GPIOx_OSPEEDR,
  *         GPIOx_PUPDR, GPIOx_AFRL and GPIOx_AFRH.
  * @note   The configuration of the locked GPIO pins can no longer be modified
  *         until the next reset.
  * @param  GPIOx: where x can be (A..K) to select the GPIO peripheral for STM32F405xx/407xx and STM32F415xx/417xx devices
  *                      x can be (A..I) to select the GPIO peripheral for STM32F42xxx/43xxx devices.
  *                      x can be (A, B, C, D and H) to select the GPIO peripheral for STM32F401xx devices. 
  * @param  GPIO_Pin: specifies the port bit to be locked.
  *          This parameter can be any combination of GPIO_Pin_x where x can be (0..15).
  * @retval None
  */
void GPIO_PinLockConfig(GPIO_TypeDef* GPIOx, uint16_t GPIO_Pin)
{
  __IO uint32_t tmp = 0x00010000;

  /* Check the parameters */
  assert_param(IS_GPIO_ALL_PERIPH(GPIOx));
  assert_param(IS_GPIO_PIN(GPIO_Pin));

  tmp |= GPIO_Pin;
  /* Set LCKK bit */
  GPIOx->LCKR = tmp;
  /* Reset LCKK bit */
  GPIOx->LCKR =  GPIO_Pin;
  /* Set LCKK bit */
  GPIOx->LCKR = tmp;
  /* Read LCKK bit*/
  tmp = GPIOx->LCKR;
  /* Read LCKK bit*/
  tmp = GPIOx->LCKR;
}

/**
  * @}
  */

/** @defgroup GPIO_Group2 GPIO Read and Write
 *  @brief   GPIO Read and Write
 *
@verbatim   
 ===============================================================================
                         ##### GPIO Read and Write #####
 ===============================================================================
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

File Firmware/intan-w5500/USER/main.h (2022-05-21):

/**
  ******************************************************************************
  * @file    Project/STM32F4xx_StdPeriph_Templates/main.h 
  * @author  MCD Application Team
  * @version V1.1.0
  * @date    18-January-2013
  * @brief   Header for main.c module
  ******************************************************************************
  * @attention
  *
  * <h2><center>&copy; COPYRIGHT 2013 STMicroelectronics</center></h2>
  *
  * Licensed under MCD-ST Liberty SW License Agreement V2, (the "License");
  * You may not use this file except in compliance with the License.
  * You may obtain a copy of the License at:
  *
  *        http://www.st.com/software_license_agreement_liberty_v2
  *
  * Unless required by applicable law or agreed to in writing, software 
  * distributed under the License is distributed on an "AS IS" BASIS, 
  * WITHOUT WARRANTIES OR CONDITIONS OF ANY KIND, either express or implied.
  * See the License for the specific language governing permissions and
  * limitations under the License.
  *
  ******************************************************************************
  */
  
/* Define to prevent recursive inclusion -------------------------------------*/
#ifndef __MAIN_H
#define __MAIN_H

/* Includes ------------------------------------------------------------------*/
#include "stm32f4xx.h"



/* Exported types ------------------------------------------------------------*/
/* Exported constants --------------------------------------------------------*/

/* Port A */
#define WIZ_RDY				GPIO_Pin_2			//in

#define WIZ_SCLK			GPIO_Pin_5			//out
#define WIZ_MISO			GPIO_Pin_6			//in
#define WIZ_MOSI			GPIO_Pin_7			//out

#define USART1_TX		GPIO_Pin_9			//out
#define USART1_RX		GPIO_Pin_10		//in

#define WIZ_SCS				GPIO_Pin_4		//out
#define WIZ_nRST			GPIO_Pin_3		//out


/* Exported macro ------------------------------------------------------------*/
/* Exported functions ------------------------------------------------------- */
void TimingDelay_Decrement(void);
void  wizchip_select(void);
void  wizchip_deselect(void);
void  wizchip_write(uint8_t wb);

#endif /* __MAIN_H */

/************************ (C) COPYRIGHT STMicroelectronics *****END OF FILE****/
